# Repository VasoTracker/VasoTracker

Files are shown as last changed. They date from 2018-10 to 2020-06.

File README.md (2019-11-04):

VasoTracker
======
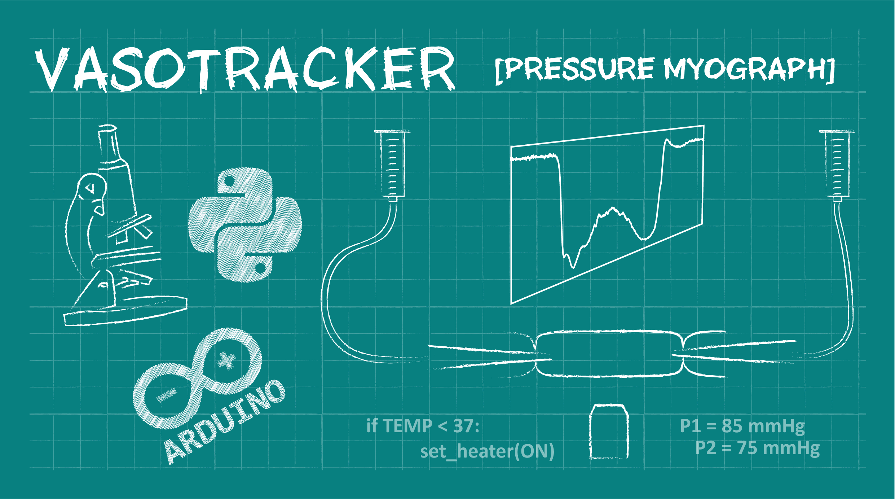
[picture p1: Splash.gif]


An open source pressure myograph system and diameter tracking software for assessing vascular reactivity.

Pressure myographs are used to assess blood vessel function. Both smooth muscle cell contraction and relaxation can be assayed using the pressure myograph.

Commercial pressure myograph systems are expensive. Rather than buy one, we prefered to build our own, taking advantage of open-source technologies and cheap off-the-shelf components. 

If you want to build your own myograph system, or simply want to try our software with an existing system, give VasoTracker a try. Its cheap (well its free) and it works.

## Paper
A paper describing the system in full, and demonstrating its use for studying vascular activity will hopefully be published in the very near future. We will place a link to the paper here: DOI:[10.3389/fphys.2019.00099](https://www.frontiersin.org/articles/10.3389/fphys.2019.00099/full)

# Contributors:
**University of Strathclyde:**
* Calum Wilson
* Matthew D Lee
* John G McCarron

**University of Durham:**
* Penelope F Lawton
* Christopher D Saunter
* John G Girkin

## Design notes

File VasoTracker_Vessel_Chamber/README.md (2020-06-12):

VasoTracker Vessel Chamber
======
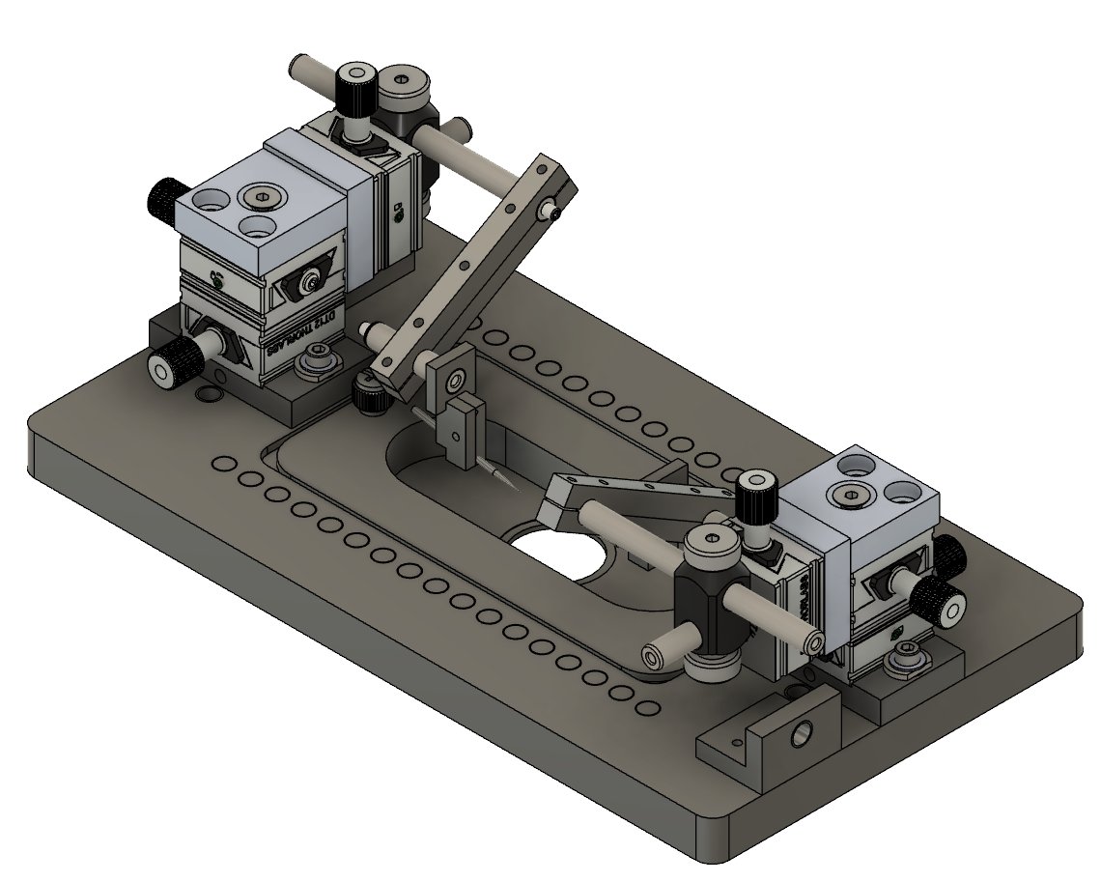
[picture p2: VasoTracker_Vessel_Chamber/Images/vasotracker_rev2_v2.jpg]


THIS IS VERSION 2 OF THE  VASOTRACKER CHAMBER. WE MAY HAVE MORE UPDATES - CHECKOUT THE VASOTRACKER WEBSITE:
http://www.vasotracker.com/downloads/pressure-myograph-hardware/

A cheap but effective vessel chamber for pressure myography. This repository contains the source files required to manufacture the Vessel Chamber.

We provide Creo (.prt), Fusion 360 (.f3d), STEP, and STL files. However, our parts were designed using Creo Parametric 4.0.  You'd be best to get a copy of Creo if you want to make any changes to the .prt files. PTC offer a free student edition: https://www.ptc.com/en/academic-program/products/free-software. However, if you only are happy with the chamber as it is then the .step files are all you need.

## Features

* **Designed for use on upright and inverted microscopes**

* **Precise alignment of cannula via 3-axis manipulators**

* **Magnetic mounts for perfusion plumbing and oxygenation**

## VasoTracker Chamber Parts:

The VasoTracker chamber can be built for less than £1300. The main chamber parts were custom designed and can be machined/3D-printed by in-house workshops or via commercial manufacturing services (e.g. Protolabs). Obviously, if you have access to a mechanical workshop, the system will be much cheaper than the price quoted below.

Here is a table of the custom components required:

  **Custom Imaging Chamber Parts**| **Material** |**Supplier**|**Part #**|**Qty**|**£/unit**|**Total (£)**
  :-----:|:-----:|:-----:|:-----:|:-----:|:-----:|:-----:
  ||||||
  Chamber base | POM-C/Delrin | Workshop / Protolabs | - | 1 |178.62|178.62
  Chamber insert | POM-C/Delrin ** | Workshop / Protolabs | - | 1 |95.48|95.48
  Leur connector blocks | POM-C/Delrin | Workshop / Protolabs | - | 2 |136.52|273.04
  Cannula fixture A | PETG/PLA | 3D Print | - | 2 | - | -
  Cannula fixture B | PETG/PLA | 3D Print | - | 2 | - | -
  Cannula Lateral Bottom | PETG/PLA | 3D Print | - | 2 | - | -
  Cannula Lateral Top | PETG/PLA | 3D Print | - | 2 | - | -
  Magnetic plumbing holders | SS or Delrin ** | Workshop / Protolabs | - | 2 | - | -
   ||||||
   | | | | | |**Subtotal**|**547.14**

* Prices correct June 2020. Obviously, they are subject to change.

Here are the other required components:

| Parts                                          | Supplier                | Part #      | Qty | £/unit   | Total (£) |
|------------------------------------------------|-------------------------|-------------|-----|----------|-----------|
|                                                |                         |             |     |          |           |
| Imaging Chamber                                |                         |             |     |          |           |
| 25mm diameter cover glass (100   pieces)       | Scientific Lab Supplies | MIC3320     | 1   | 18.66    | 18.66     |
| M3 thumb screws (Come in a   pack of 10)       | RS                      | 664-4637    | 1   | 4.7      | 4.7       |
|                                                |                         |             |     |          |           |
| Perfusion attachments                          |                         |             |     |          |           |
| 5mm diameter, 3mm thick disc magnets (50 pk)   | Amazon                  | B00TACMMP0  | 1   | 7.20     | 7.20      |
| 1.5", 14 - 18 Guage Blunt, bent needles        | Needlez                 | Selection   | -   | -        | -         |
| Superglue                                      | Amazon                  | B003CT4XT0  | 1   | 4.20     | 4.20      |
|                                                |                         |             |     |          |           |
| Cannula holders                                |                         |             |     |          |           |
| 3-axis translation stage                       | Thorlabs                | DT12XYZ/M   | 2   | 245.91   | 491.82    |
| Screw thread adapter                           | Thorlabs                | AP4M3M      | 2   | 1.58     | 3.16      |
| 13 mm metal rod                                | Thorlabs                | MS05R/M     | 2   | 4.79     | 9.58      |
| 25 mm metal rod                                | Thorlabs                | MS1R/M      | 2   | 5.08     | 10.16     |
| 75 mm metal rod                                | Thorlabs                | MS3R/M      | 2   | 6.34     | 12.68     |
| 90 degree rod clamp                            | Thorlabs                | MSRA90      | 2   | 13.39    | 26.78     |
| 1.5 mm OD glass capillary glass (225 pieces)   | Warner Instruments      | 30-0058     | 1   |          |           |
| M2 Screw & nut kit                             | Amazon                  | B07TNT5NMY  | 1   | 5.99     | 5.99      |
|                                                |                         |             |     |          |           |
| Tubing & Connectors                            |                         |             |     |          |           |
| Female luer  (threaded 1/16" barb; pack of 25) | Cole-Palmer             | GY-45502-30 | 1   | 8.53     | 8.53      |
| Masterflex 1.22 ID tubing (100   ft roll)      | Cole-Palmer             | WZ-06460-31 | 1   | 96       | 96        |
| Female luer (1/16" barb;   pack of 25)         | Cole-Palmer             | GY-45502-00 | 1   | 6.36     | 6.36      |
| Male luer (1/16" barb;   pack of 25)           | Cole-Palmer             | GY-45505-00 | 1   | 6.46     | 6.46      |
| Luer stopcock (pack of 10)                     | Cole-Palmer             | WZ-30600-02 | 1   | 16.94    | 16.94     |
|                                                |                         |             |     |          |           |
|                                                |                         |             |     | Subtotal | 712       |

* Prices correct June 2020. Obviously, they are subject to change.

## Building the VasoTracker Chamber:

 To build the VasoTracker chamber, all that is required it to connect the components together:

 1.	Seal the bottom of the chamber insert by securing a 25mm coverslip to the through-hole using superglue or vacuum grease.
 2.	Place the chamber insert in the chamber base and secure using 2 of the M3 thumb screws.
 3.	Secure the tubing anchors to the chamber base using M3 screws.
 4.	Secure 5 mm diameter magnets into the holes on the chamber base using superglue. You may want to ensure that the polarity of all of the magnets is the same.
 5.	Secure 5 mm diameter magnets into the bottom of plumbing holders using superglue. You may want to ensure that the polarity is correct.
 5.	Secure the mounts for the 3-axis positioning stages to the base using the included M6 screws. Then mount the 3-axis positioning stages.
 6. Connect the cannula holder parts to the 3-axis manipulators as shown below.
 7.	Mount glass cannula (pulled with pipette puller) onto cannula holder.
 8. Screw a threaded female luer (1/16" barb) into each of the tubing holders.
 9. Connected cannula to luer connector via tubing.
 10. Connect luer stopcock to each of the leur connectors to enable 3-way control of input and output.
 11. Securse bent needle perfusion plumbing in magnetic holders and the chamber is ready to be filled with physiological saline solution!

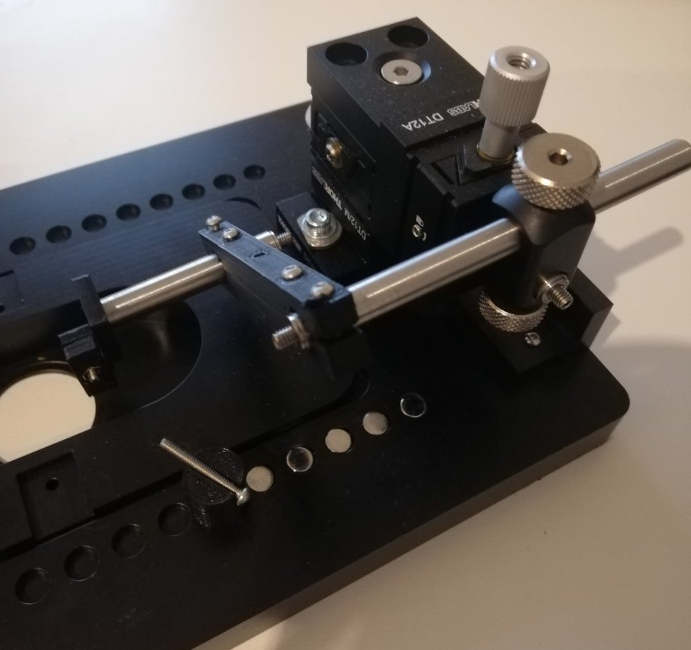
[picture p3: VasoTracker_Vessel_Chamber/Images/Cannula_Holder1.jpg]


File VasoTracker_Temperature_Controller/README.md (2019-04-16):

VasoTracker Temperature Controller
======


An Arduino-based temperature controller for the VasoTracker myograph system.

## Features

* **Reads and displays temperature sensed by an 10k NTC thermistor**

* **Implements bang-bang control of heating elements mounted on the VasoTracker Vessel Chamber**

* **Writes data to serial port for acquisition and display by the VasoTracker GUI**

## Required components:

The VasoTracker Temperature Controller (with temperature sensor and two heating elements) can be built for ~£75. Here is a table of the components required:

**Parts**|**Supplier**|**Part #**|**Qty**|**£/unit**|**Total (£)**
:-----:|:-----:|:-----:|:-----:|:-----:|:-----:
Arduino Uno|Arduino|A000066 |1|20.7|20.7
12V power supply|RS|903-7048|1|12.68|12.68
Arduino Proto Shield |Arduino|A000077|1|10|10
LCD Shield|iTead Studio|1602 LCD|1|3.98|3.98
10k NTC Thermistor|Adafruit|372|1|3.03|3.03
Kool-Pak 0.2Ω Thick Film (Heating) Resistor|Caddock|MP825.20.0-1%|2|6.89|13.78
NPN MOSFET|Infineon Technologies|IRL540NPBF|1|0.99|0.99
Resistor kit|Velleman-kit|RES-E12|1|4.7|4.7
Jumper wire kit|RobotShop|RB-Cix-02|1|3.77|3.77
2-pin Screw Terminal|RobotShop|RB-Dfr-465|3|0.6|1.8
Arduino R3 Stackable Headers|Sparkfun Electronics|PRT-10007|1|1.14|1.14
LEGO™ Encolsure|LEGO|-|-|-|-
 | | | |**Subtotal**|**76.57**

## Building the VasoTracker Temperature Controller:

To build the temperature controller, there is a little bit of soldering involved:

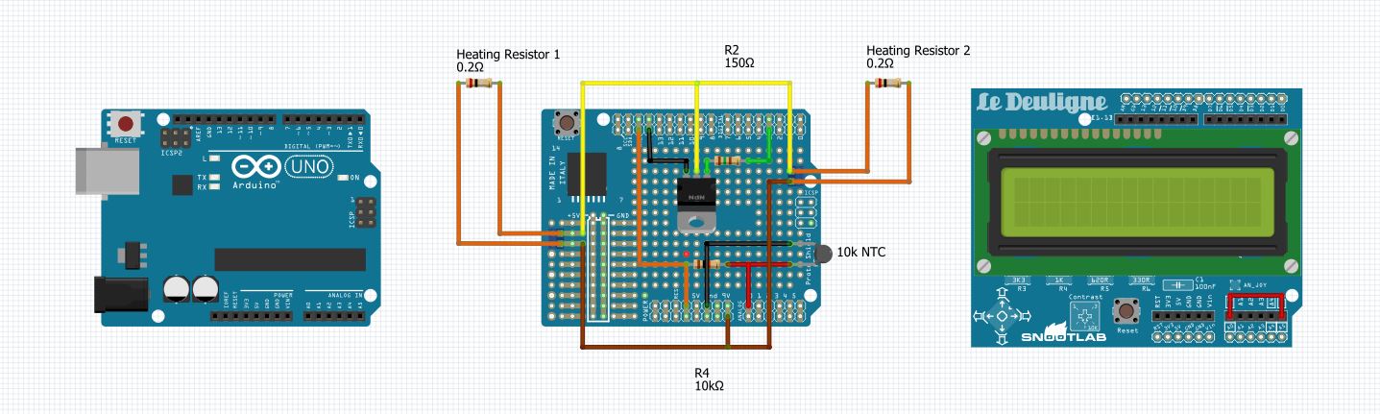
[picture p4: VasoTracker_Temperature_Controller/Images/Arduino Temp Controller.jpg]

</br>
Temperature controller schematic created using the breadboard view in Fritzing (http://fritzing.org/home/)

1.	Build the temperature sensor / heating circuit on the Arduino Proto shield, as shown in image above. Note that the heating elements (resistors) are connected to the Temperature controller via jumper cables and screw terminals mounted on the Proto Shield. Similarly, the temperature sensor is connected to a screw terminal mounted on the Proto Shield.
2.	Stack the completed Proto shield on top of the Arduino Uno.
3.	Place stackable headers on top of the Proto Shield (these are required to allow clearance for the pressure transducer connections and bend the A0 pin1 on the stackable header so that it does not connect to the Arduino Uno board.
4.	Stack the LCD Shield on top of the stackable headers.
5.	Use a female 1-pin jumper cable to connect the disconnected pin on the stackable header to the A5 pin on top of the LCD shield.
6.	 Wrap one end of a wire around the Arduino reset pin and another around Vin (5V).
7.	 Stack the LCD shield on top of the Arduino.
8.	 Connect a power supply to the ARDUINO device to switch the unit on. To supply sufficient power, it is recommended to use a 12V wall wort power supply, and to use the USB cable for data transmission.
9.	 Optionally, the device may be placed in an enclosure. We chose to build one from Lego® blocks because of their versatility .

**Notes:**
1. The A000077 Proto Shield is being discontinued. Many other suppliers sell equivalent prototyping boards (e.g. Adafruit 2077 Proto Shield).
2. For pictures of Step 3 onwards, check the similar instructions for the pressure controller here: https://github.com/VasoTracker/VasoTracker/tree/master/VasoTracker_Pressure_Monitor)**
2. The LCD shield uses the A0 pin for buttons. However, we (stupidly) connected our thermistor to A0. By bending the A0 pin on the stackable header and connecting it to A5 on the LCD shield, we are rerouting A0 on the LCD shield to A5 (thus enabling the thermistor to use A0). Obviously, by connecting the thermistor to A5, and altering the Arduino code, this step could be avoided!
3. Should prevent accidental resetting of the Arduino (which would be annoying if it occurred during an experiment)... connect reset pin to 5V via 120 ohm resistor
4. As an alternative to soldering the components onto the Arduino Proto Shield, an Arduino Proto Shield with Mini Breadboard could be used.

## Programming the VasoTracker Temperature Controller:

   * Download VasoTracker as a zip file and extract all files (if you don't have it already) from here: https://github.com/kaelome/VasoTracker
   * Download and install the Aruino IDE (Python 3.6) <https://www.arduino.cc/en/Guide/Windows#toc1>
   * Open the following Arduino file in the Arduino IDE: VasoTracker/VasoTracker_Temperature_Controller/VasoTracker_Temperature_Controller_Code/VasoTracker_Temperature_Controller_Code.ino
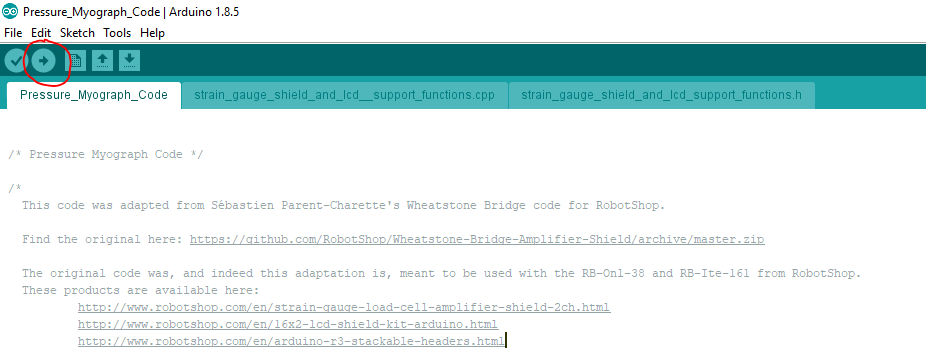
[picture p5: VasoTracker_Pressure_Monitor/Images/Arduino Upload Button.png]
   *	Upload code to the Arduino by clicking the upload button 

### Setting up the VasoTracker Temperature Controller:

  * Ensure heating elements are secured to the Vessel Chamber
  * Place temperature sensor in the Vessel Chamber (it is held in place by a magnetic clamp)
  * Connect the heating elements to the Temperature Controller.
  * Connect Temperature Controller to data acquisition computer via Arduino USB cable.
  * Connect 12V power supply to the Arduino
  * Adjust setpoint to desired temperature using LCD buttons

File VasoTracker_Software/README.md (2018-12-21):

VasoTracker diameter tracking software
======
Software for automatic diameter tracking in pressure myography experiments.

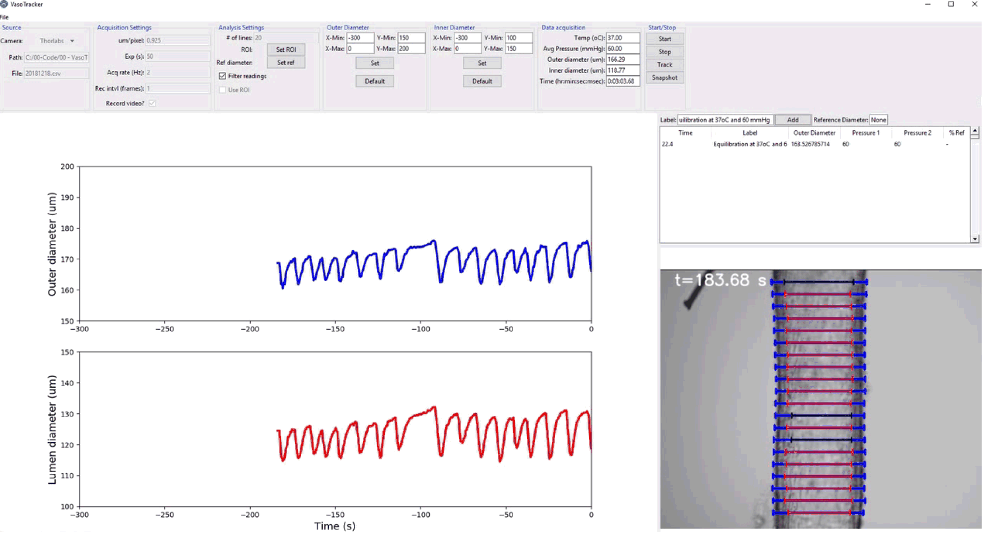
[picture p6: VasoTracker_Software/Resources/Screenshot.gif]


Written in [Python 2.7](https://www.python.org/ "Python 2.7"), and making use of [μManager](https://micro-manager.org/) camera control libraries

## Features

* **Acquires diameter measurements from pressurised blood vessels**

* **Live graphing of both outer and inner blood vessel diameter**

* **Diameter indicators overlaid on live image feed**

* **Synchronised data collection records and displays diameter, pressure, and temperature readings**

* **Record diameter measurements from up to 50 scan lines (you can examine propagated dilations)**

* **Line averaging: each scan line is integrated over 25 pixel lines to minimise errors introduced by contrast variances, the average diameter at each scanline is calculated and plotted**

* **Limit diameter tracking to a region of interest**

* **Filter of diameter measurements to exclude outlier data points**

* **Record and save image data throughout the experiment: VasoTracker outputs raw .tiff files, and .tiff files with diameter indicators overlaid**

* **All data is conveniently and automatically exported to .csv format**

* **Use with your own hardware! So long as your camera works with [μManager](https://micro-manager.org/), it can work with VasoTracker**

## Installing the VasoTracker Software:

A handy single-file installer and instructions for using the VasoTracker software is available to download at our [VasoTracker](http://www.vasotracker.com/downloads/) website.

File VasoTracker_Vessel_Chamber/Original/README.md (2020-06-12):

VasoTracker Vessel Chamber
======
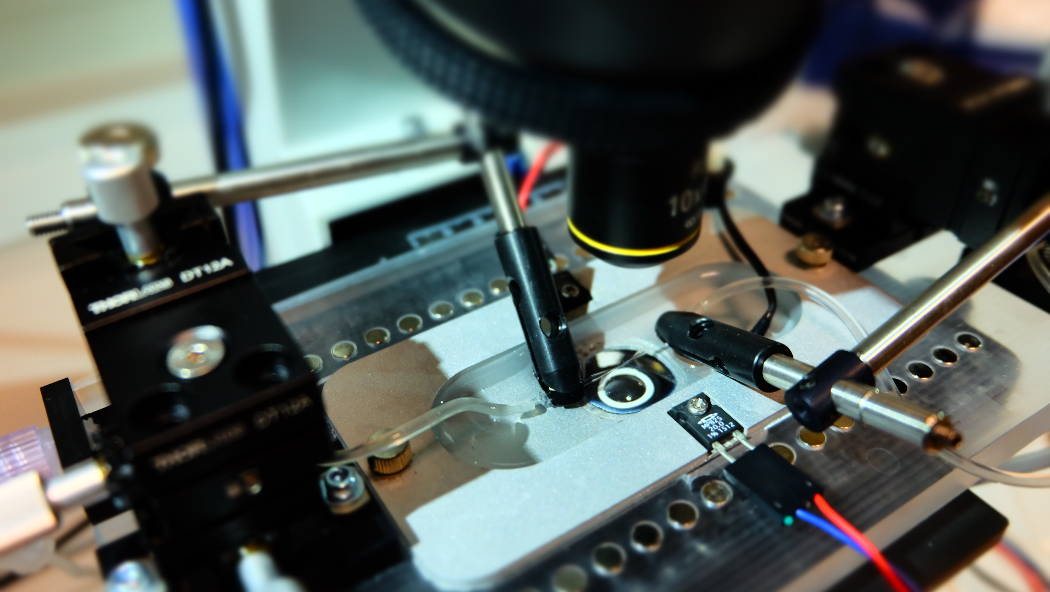
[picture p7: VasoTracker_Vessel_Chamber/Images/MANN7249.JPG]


## THIS IS THE ORIGINAL VASOTRACKER CHAMBER. FOR THE LATEST VASOTRACKER CHAMBER DESIGN, CHECKOUT THE VASOTRACKER WEBSITE:
http://www.vasotracker.com/downloads/pressure-myograph-hardware/

A cheap but effective vessel chamber for pressure myography. This repository contains the source files required to manufacture the Vessel Chamber.

These contents of this repository were designed using Creo Parametric 4.0. You'll need a copy of Creo if you want to make any changes to the .prt files. PTC offer a free student edition: https://www.ptc.com/en/academic-program/products/free-software. However, if you only are happy with the chamber as it is then the .step files are all you need.

## Features

* **Designed for use on upright and inverted microscopes**

* **Precise alignment of cannula via 3-axis manipulators**

* **Compatible with Built-in heating system:** (https://github.com/kaelome/VasoTracker/tree/master/VasoTracker_Temperature_Controller)

* **Magnetic mounts for perfusion plumbing and oxygenation**

## Building the VasoTracker Pressure Monitor:

The VasoTracker pressure monitor (with two inline pressure transducers) can be built for ~ £1500. The main chamber has been custom designed and can be machined by in-house workshops or via commercial manufacturing services (e.g. Protolabs). Obviously, if you have access to a mechanical workshop, the system will be much cheaper than the price quoted below.

Here is a table of the custom components required:

  **Custom Imaging Chamber Parts**| **Material** |**Supplier**|**Part #**|**Qty**|**£/unit**|**Total (£)**
  :-----:|:-----:|:-----:|:-----:|:-----:|:-----:|:-----:
  ||||||
  Chamber base | PMMA | Workshop / Protolabs | - | 1 |174.39|174.39
  Chamber insert | SS or Delrin ** | Workshop / Protolabs | - | 1 |144.21|144.21
  Tubing anchors | PMMA | Workshop / Protolabs | - | 2 |123.94|247.88
   ||||||
   | | | | |**Subtotal**|**442.54**

** This part should be machined from stainless steel (SS) if the VasoTracker Temperature Controller is to be used. If other temperature control methods will be used (e.g. externally heated perfusion solution), this part can be machined from Delrin (POM-C)

Here are the other required components:

| Parts                                          | Supplier                | Part #      | Qty | £/unit   | Total (£) |
|------------------------------------------------|-------------------------|-------------|-----|----------|-----------|
|                                                |                         |             |     |          |           |
| Imaging Chamber                                |                         |             |     |          |           |
| 25mm diameter cover glass (100   pieces)       | Scientific Lab Supplies | MIC3320     | 1   | 18.66    | 18.66     |
| M3 thumb screws (Come in a   pack of 10)       | RS                      | 664-4637    | 1   | 4.7      | 4.7       |
|                                                |                         |             |     |          |           |
| Perfusion attachments                          |                         |             |     |          |           |
| Neodynium disc magnets (In a   pack of 10)     | RS                      | 792-4559    | 4   | 4.15     | 16.6      |
| Magnetic Clamp for suction   tubes             | Warner Instruments      | MAG-2       | 4   | 45.00    | 180.00    |
|                                                |                         |             |     |          |           |
| Cannula holders                                |                         |             |     |          |           |
| 3-axis translation stage                       | Thorlabs                | DT12XYZ/M   | 2   | 231.80   | 463.60    |
| Screw thread adapter                           | Thorlabs                | AP4M3M      | 4   | 1.48     | 5.92      |
| 13 mm metal rod                                | Thorlabs                | MS05R/M     | 2   | 4.51     | 9.02      |
| 38 mm metal rod                                | Thorlabs                | MS1.5R/M    | 2   | 4.93     | 9.86      |
| 75 mm metal rod                                | Thorlabs                | MS3R/M      | 2   | 5.97     | 11.94     |
| 90 degree rod clamp                            | Thorlabs                | MSRA90      | 2   | 12.62    | 25.24     |
| 90 degree rod clamp                            | Thorlabs                | ER90B/M     | 2   | 10.71    | 21.42     |
| Cannula holder                                 | Siskiyou                | MSC-1 M     | 2   | 21.00    | 42.00     |
| 1.5 mm OD glass capillary   glass (225 pieces) | Harvard Apparatus       | 300058      |     |          |           |
|                                                |                         |             |     |          |           |
| Tubing & Connectors                            |                         |             |     |          |           |
| Female luer  (threaded 1/16" barb; pack of 25) | Cole-Palmer             | GY-45502-30 | 1   | 8.53     | 8.53      |
| Masterflex 1.22 ID tubing (100   ft roll)      | Cole-Palmer             | WZ-06460-31 | 1   | 96       | 96        |
| Female luer (1/16" barb;   pack of 25)         | Cole-Palmer             | GY-45502-00 | 1   | 6.36     | 6.36      |
| Male luer (1/16" barb;   pack of 25)           | Cole-Palmer             | GY-45505-00 | 1   | 6.46     | 6.46      |
| Luer stopcock (pack of 10)                     | Cole-Palmer             | WZ-30600-02 | 1   | 16.94    | 16.94     |
|                                                |                         |             |     |          |           |
|                                                |                         |             |     | Subtotal | 943.25    |

 To build the VasoTracker chamber, all that is required it to connect the components together:

 1.	Seal the bottom of the chamber insert by securing a 25mm coverslip to the through-hole using superglue or vacuum grease.
 2.	Place the chamber insert in the chamber base and secure using 2 of the M3 thumb screws.
 3.	Secure the tubing anchors to the chamber base using M3 screws.
 4.	Secure 10 mm diameter magnets into the holes on the chamber base using superglue. You may want to ensure that the polarity of all of the magnets is the same.
 5.	Secure the mounts for the 3-axis positioning stages to the base using the included M6 screws. Then mount the 3-axis positioning stages.
 6. Screw each of the cannula holders onto a 38 mm rod and couple to the 3-axis manipulators as shown below:
 7.	Mount glass cannula (pulled with pipette puller) onto cannula holder.
 8. Screw a threaded female luer (1/16" barb) into each of the tubing holders.
 9. Connected cannula to luer connector via tubing.
 10. Connect luer stopcock to each of the leur connectors to enable 3-way control of input and output.
 11. The chamber is now ready to be filled with physiological saline solution and have an artery mounted between the two cannula!

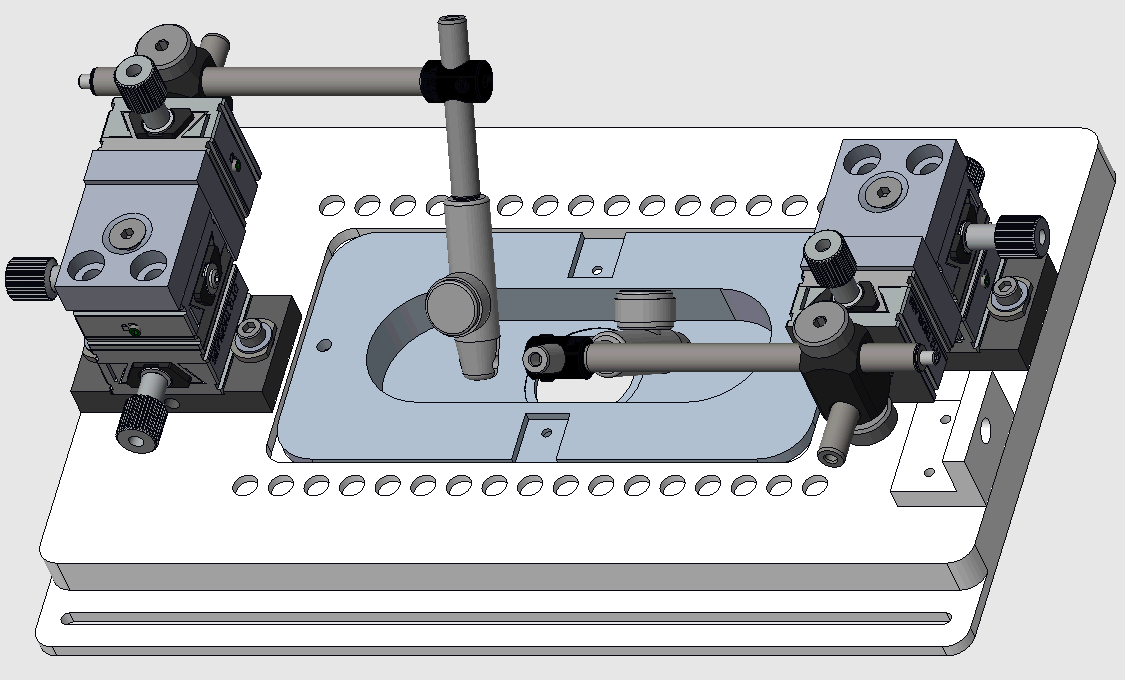
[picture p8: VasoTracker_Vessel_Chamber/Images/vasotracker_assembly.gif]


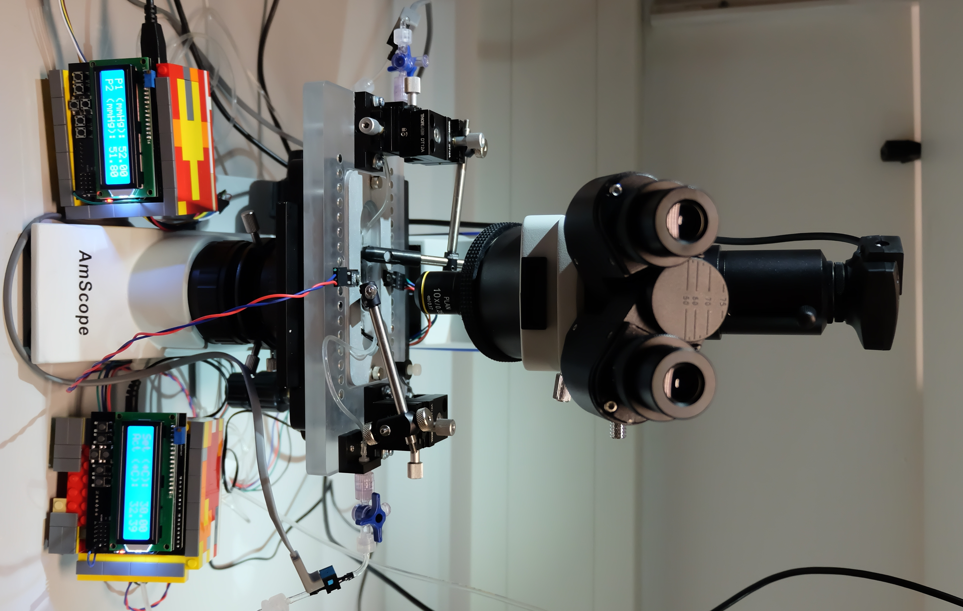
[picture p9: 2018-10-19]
VasoTracker_Vessel_Chamber/Images/MANN7244_cropped.jpg

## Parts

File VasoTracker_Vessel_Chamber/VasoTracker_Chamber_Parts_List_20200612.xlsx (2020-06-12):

Myograph Bath
Parts | Supplier | Part # / Description | Qty | £/unit | Total (£)
Custom Imaging Chamber Parts
Chamber | ProtoLabs | CNC Machine - POM-C, METRIC THREADING (SEE DRAWINGS FOR THREADING) | 1 | 178.62 | 178.62
Chamber insert | ProtoLabs | CNC Machine - POM-C, METRIC THREADING (SEE DRAWINGS FOR THREADING) | 1 | 95.48 | 95.48
Leur connector blocks | Protolabs | CNC Machine - POM-C, METRIC THREADING (SEE DRAWINGS FOR THREADING) | 2 | 136.52 | 273.04
Cannula fixture A | - | 3D Print (ETG/PLA) | 2 | - | - | 547.14
Cannula fixture B | - | 3D Print (ETG/PLA) | 2 | - | -
Cannula Lateral Bottom | - | 3D Print (ETG/PLA) | 2 | - | -
Cannula Lateral Top | - | 3D Print (ETG/PLA) | 2 | - | -
Magnetic plumbing holders | - | 3D Print (ETG/PLA) | 3 | - | -
Imaging Chamber Parts
25 mm Diameter No 1 Coverslips | Amazon | SLS MIC3320 | 1 | 18.66 | 18.66
M3 Thumb Screws, 6-10 mm long | Amazon | www.amazon.co.uk/sourcingmap%C2%AE-Computer-M3x7mm-Aluminum-Knurled/dp/B01NBDUK82/ | 1 | 5 | 5
Perfusion Attachments
50 Magnets | Amazon | 5mm diameter, 3 mm thick, www.amazon.co.uk/gp/product/B00TACMMP0 | 1 | 7.2 | 7.2
1.5", 14 - 18 Guage Blunt, bent needles | Needlez | For perfusion plumbing, get a selection, https://www.needlez.co.uk/product/16g-blunt-needle-1-5inch-38mm-bent-tip-90-deg | 2 | 0.63 | 1.26
Superglue | Amazon | Gorilla Glue, https://www.amazon.co.uk/Gorilla-4044205-Superglue-15g/dp/B003CT4XT0/ | 1 | 4.2 | 4.2
Cannula holders
3-axis MicroManipulator | Thorlabs | DT12XYZ/M | 2 | 245.91 | 491.82
Screw thread adapter | Thorlabs | AP4M3M | 2 | 1.58 | 3.16
13 mm metal rod | Thorlabs | MS05R/M | 2 | 4.79 | 9.58
25 mm metal rod | Thorlabs | MS1R/M | 2 | 5.08 | 10.16
75 mm metal rod | Thorlabs | MS3R/M | 2 | 6.34 | 12.68
90 degree clamp | Thorlabs | MSRA90 | 2 | 13.39 | 26.78
1.5 mm OD glass capillary glass (225 pieces) | Warner Instruments30-0058 |  | 1 | -
M2 Screw Kit | Amazon | Variety hex screws and nuts, www.amazon.co.uk/gp/product/B07TNT5NMY/ | 1 | 5.99 | 5.99
Tubing & Connectors
Female luer (threaded 1/16" barb; pack of 25) | Cole-Palmer | GY-45502-30 | 1 | 8.53 | 8.53
Masterflex 1.22 ID tubing (100 ft roll) | Cole-Palmer | WZ-06460-31 | 1 | 96 | 96
Female luer (1/16" barb; pack of 25) | Cole-Palmer | GY-45502-00 | 1 | 6.36 | 6.36
Male luer (1/16" barb; pack of 25) | Cole-Palmer | GY-45505-00 | 1 | 6.46 | 6.46
Luer stopcock (pack of 10) | Cole-Palmer | WZ-30600-02 | 1 | 16.94 | 16.94
 |  |  |  | Subtotal | 1277.92

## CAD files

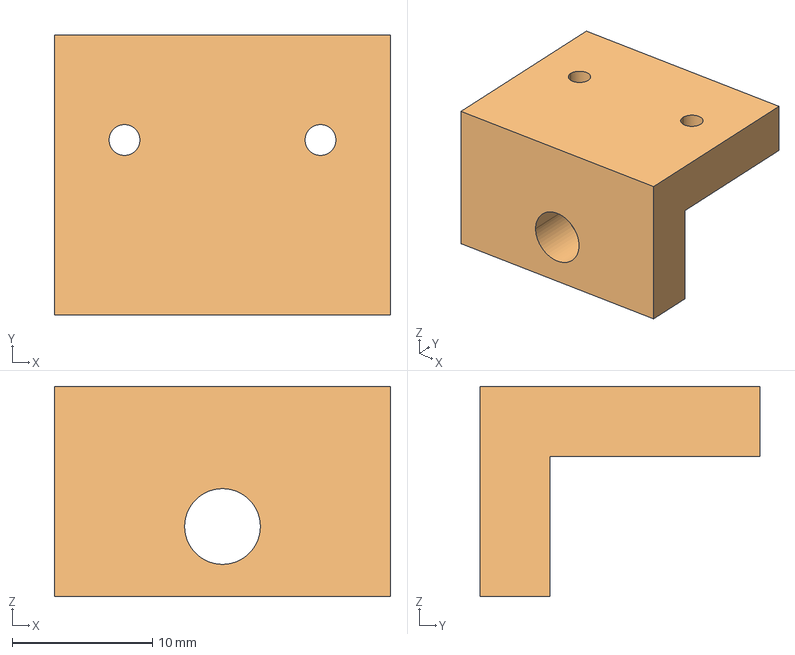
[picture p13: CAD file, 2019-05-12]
VasoTracker_Vessel_Chamber/Original/REV2/STEP/tubing_anchor.stp
24.0 x 20.0 x 15.0 mm

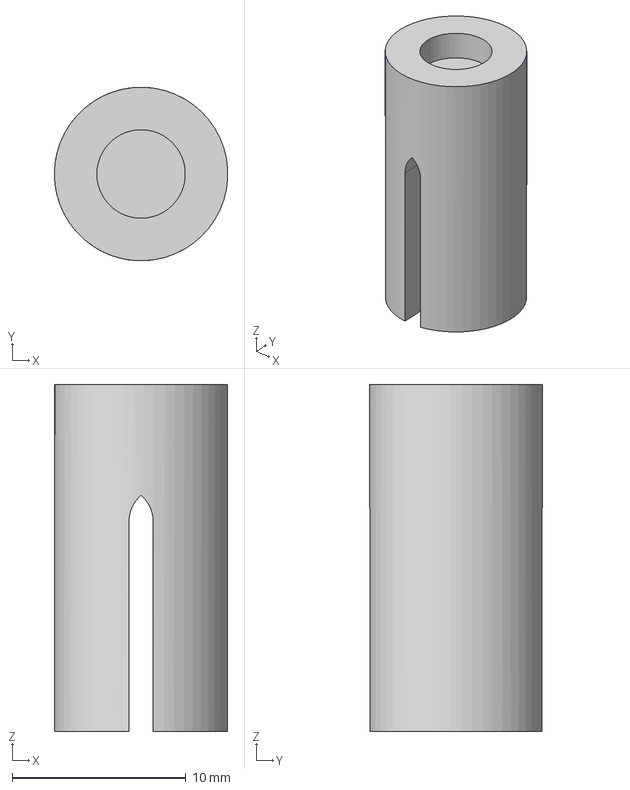
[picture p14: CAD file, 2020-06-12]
VasoTracker_Vessel_Chamber/Step/puming_holder_large v2.step
9.99 x 10.0 x 20.0 mm

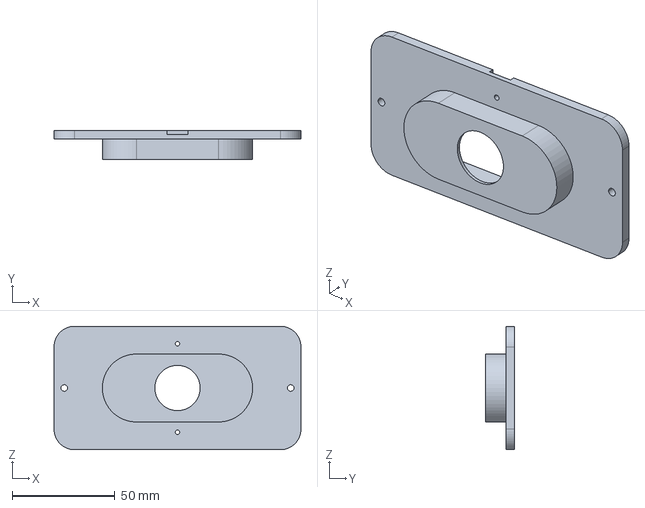
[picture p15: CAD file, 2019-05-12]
VasoTracker_Vessel_Chamber/Original/REV2/STEP/chamber_insert.stp
120.0 x 14.0 x 60.0 mm

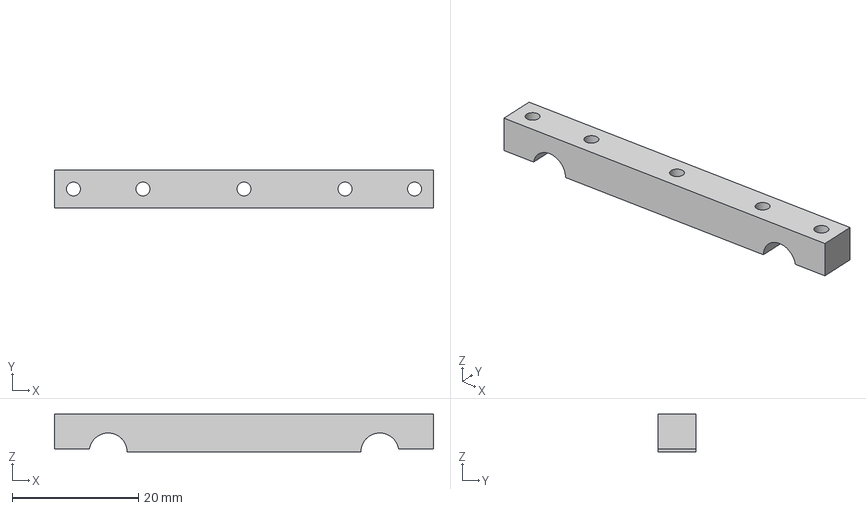
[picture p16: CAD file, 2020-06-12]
VasoTracker_Vessel_Chamber/Step/CANNULA_ARM_B v1.step
60.0 x 6.00 x 6.00 mm

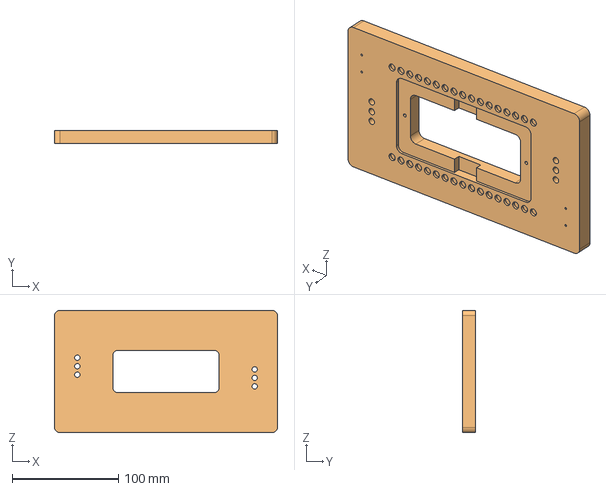
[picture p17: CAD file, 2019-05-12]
VasoTracker_Vessel_Chamber/Original/REV2/STEP/chamber_base.stp
210.0 x 12.0 x 115.0 mm

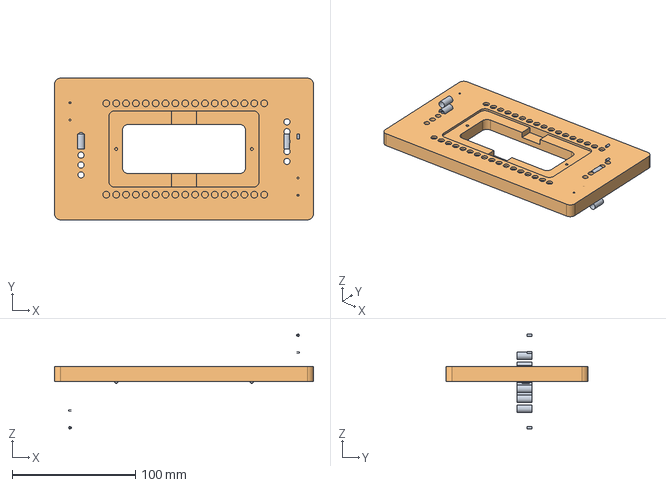
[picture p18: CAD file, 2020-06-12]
VasoTracker_Vessel_Chamber/Step/CHAMBER_BASE_REV2 v2.step
210.0 x 115.0 x 77.0 mm

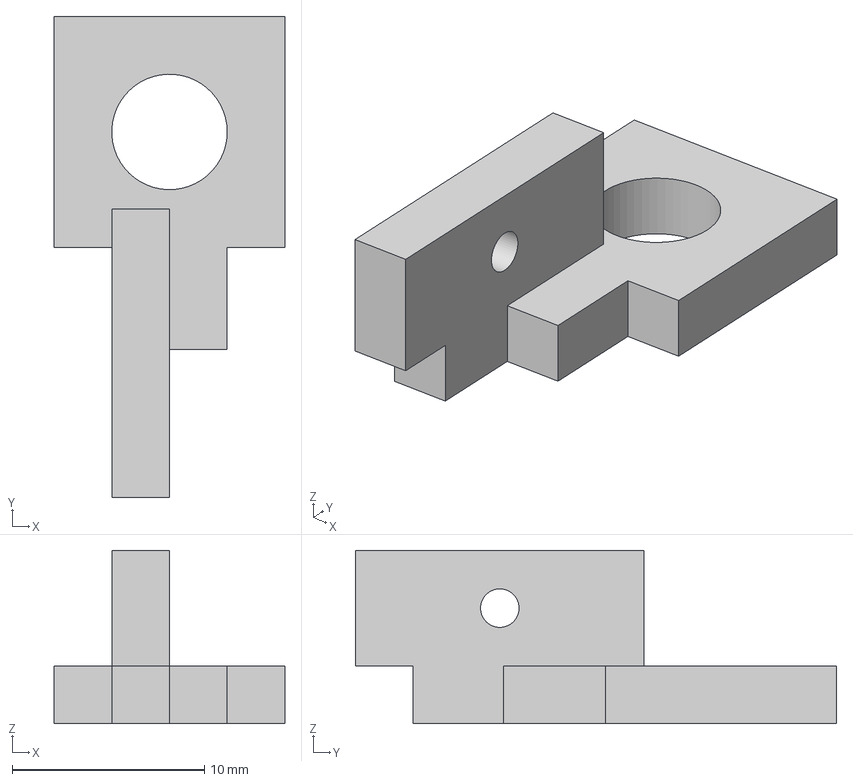
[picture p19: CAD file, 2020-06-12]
VasoTracker_Vessel_Chamber/Step/CANNULA_CLAMP_A v2.step
12.0 x 25.0 x 9.00 mm

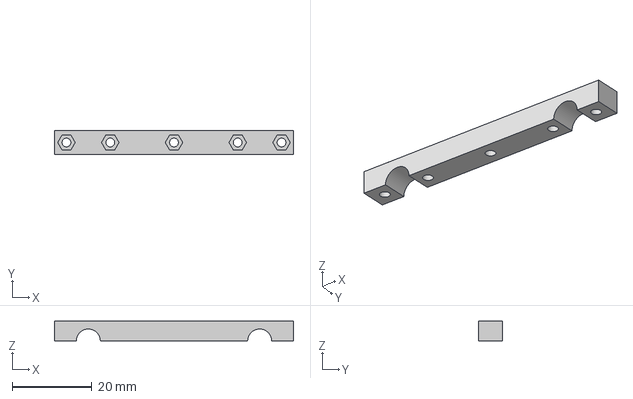
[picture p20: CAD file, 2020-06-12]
VasoTracker_Vessel_Chamber/Step/CANNULA_ARM_A v1.step
60.0 x 6.00 x 5.00 mm

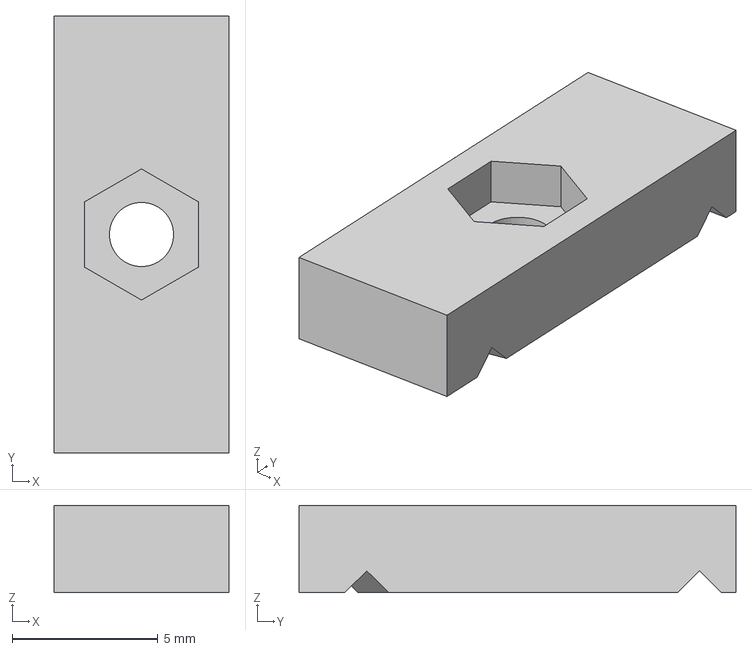
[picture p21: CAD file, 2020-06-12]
VasoTracker_Vessel_Chamber/Step/CANNULA_CLAMP_B v2.step
6.00 x 15.0 x 3.00 mm

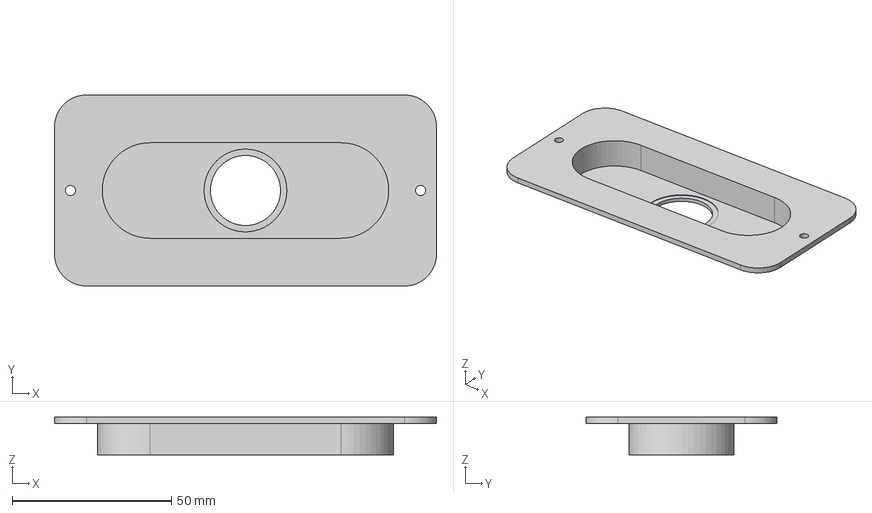
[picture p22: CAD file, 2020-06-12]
VasoTracker_Vessel_Chamber/Step/CHAMBER_INSERT_REV2_25ML v2.step
120.0 x 60.0 x 11.8 mm

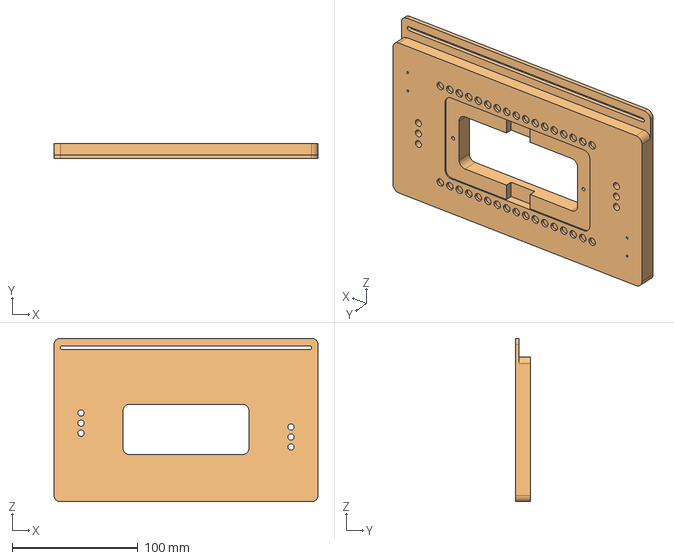
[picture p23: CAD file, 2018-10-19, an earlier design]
VasoTracker_Vessel_Chamber/Original/REV1/STEP/VasoTracker_ChamberBase.stp
210.0 x 12.0 x 130.0 mm

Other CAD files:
VasoTracker_Vessel_Chamber/Step/TUBING_ANCHOR v2.step
VasoTracker_Vessel_Chamber/Old_design/REV1/STEP/VasoTracker_TubingAnchor.stp
VasoTracker_Vessel_Chamber/Original/REV1/STEP/VasoTracker_TubingAnchor.stp
VasoTracker_Vessel_Chamber/Old_design/REV1/STEP/VasoTracker_ChamberInsert.stp
VasoTracker_Vessel_Chamber/Fusion 360/CANNULA_ARM_A v1.f3d
VasoTracker_Vessel_Chamber/Fusion 360/CANNULA_ARM_B v1.f3d
VasoTracker_Vessel_Chamber/Fusion 360/CANNULA_CLAMP_A v2.f3d
VasoTracker_Vessel_Chamber/Fusion 360/CANNULA_CLAMP_B v2.f3d
VasoTracker_Vessel_Chamber/Fusion 360/CHAMBER_BASE_REV2 v2.f3d
VasoTracker_Vessel_Chamber/Fusion 360/CHAMBER_INSERT_REV2_25ML v2.f3d
VasoTracker_Vessel_Chamber/Fusion 360/TUBING_ANCHOR v2.f3d
VasoTracker_Vessel_Chamber/Fusion 360/puming_holder_large v2.f3d
VasoTracker_Vessel_Chamber/Fusion 360/vasotracker_rev2 v2.f3d
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

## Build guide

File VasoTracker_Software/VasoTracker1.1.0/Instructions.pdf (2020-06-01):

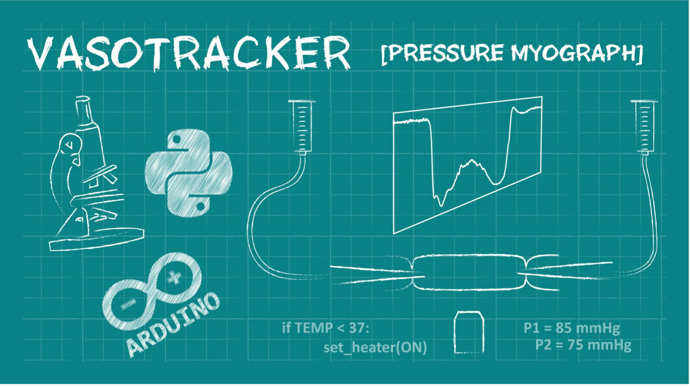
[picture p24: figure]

# Data Acquisition Software User Manual

15/11/2019

Developed at the University of Strathclyde and Durham University

www.vasotracker.com

# Table of Contents

I. Overview | 2

VasoTracker
Citing VasoTracker
The VasoTracker data acquisition software
The VasoTracker Offline Analyzer
II. | Installation | 4
| Hardware requirements
| Supported cameras Installation prerequisites
| Installing VasoTracker
III. | Running VasoTracker | 6
| Setting up a VasoTracker shortcut
| Maximizing VasoTracker performance Starting the VasoTracker Data Acquisition Software
IV. | VasoTracker Settings | 9
| The settings bar
| Source control panel Acquisition Settings control panel
| Analysis Settings control panel Outer and Inner Diameter Graph Settings control panel
| Data Acquisition panel Start/Stop panel
| Image dimension panel
V. VasoTracker Data Export | 13
| Data export Data entry table
VI. | Editing VasoTracker | 14
| Source code installation steps
| Installing Prerequisites
| Installing Python 2.7 Installing Python dependencies
| Launching VasoTracker from the source code

VASOTRACKER USER MANUAL V1 | 2

## Overview

VasoTracker

VasoTracker is an open source pressure myograph system for tracking the diameter of isolated, pressurized blood vessels. The complete system includes a vessel chamber, temperature controller, pressure monitor, microscope, camera, laptop computer, and analysis software – everything that is required to perform pressure myography.

We made VasoTracker because we wanted to make pressure myography more accessible (i.e. cheaper) and customizable. The full system costs ~$4500 (£3500 if you are in the UK). This is ~10% of the cost of a commercial myograph system. Visit the VasoTracker website (www.vasotracker.com) to find out how to build your own.

Citing VasoTracker

We hope that VasoTracker is of use to you or anyone else wishing to study blood vessel function. Our work developing and releasing VasoTracker as an open source platform was made possible by grant funding from the Wellcome Trust and British Heart Foundation. Our ability to support, develop and maintain VasoTracker will depend on more grants, so whether you use the VasoTracker software and hardware as a complete system or only the certain bit, please cite VasoTracker in your scientific publications.

Penelope F. Lawton, Matthew D. Lee, Christopher D. Saunter, John M. Girkin, John G. McCarron and Calum Wilson (2019). VasoTracker, a low-cost and open source pressure myograph system for vascular physiology. Frontiers in Physiology 10:99.
DOI: https://doi.org/10.3389/fphys.2019.00099

VASOTRACKER USER MANUAL V1 | 3

The VasoTracker data acquisition software

The VasoTracker data acquisition software was designed to monitor the diameter of blood vessels mounted in a pressure myograph. We developed the software to complement our own open source pressure myograph chamber, but it can be used to add diameter tracking capabilities to almost any microscope/camera set up. The software performs the following functions

- Live acquisition/display of pressurized arteries mounted in the VasoTracker vessel chamber.
- Real-time measurement and display of outer and inner artery diameter.
- Real-time measurement of bath temperature and intraluminal pressure.
- Live recording and graphing of artery diameter(s).
- Tracking of experimental manipulations (e.g. drug additions).
- Multi-line diameter tracking.
- Tracking within a user-specified region-of-interest (ROI).
- Line averaging and statistical filtering of result.
- Video output (.tiff files).

The VasoTracker Offline Analyzer

We also wrote some software for analyzing pre-recorded blood vessel data. Our offline analyzer can be used to assess vascular reactivity in blood vessels imaged using a variety of experimental techniques (pressure myography, fluorescence imaging, ultrasound). For more information and to download this software visit: http://www.vasotracker.com/blood-vessel-diameter-software/

The VasoTracker software is easy to adapt. Get in touch with us if you wish the software to calculate and output any other parameters (e.g. wall thickness, cross sectional area, media/lumen ratio). Alternatively, you can adapt the software yourself!

VASOTRACKER USER MANUAL V1 | 4

## Installation

Hardware requirements

VasoTracker is only compatible with 64-bit Windows operating systems. (well, we have only tested it on 64-bit operating systems)

- Microsoft Windows 10 Pro 64-bit
- 8GB RAM minimum (preferably 16GB)
- Compatible USB camera (see below)

Supported cameras

VasoTracker utilizes camera libraries provided by Micro-Manager (µManager) Open Source Microscopy Software (https://micro-manager.org/). If your camera works in µManager, then it should work with VasoTracker. We have fully tested, and use on our VasoTracker systems, the following cameras:

- Thorlabs DCC1545M USB 2.0 Camera
- OpenCV cameras
- FakeCamera – use to load your own images into VasoTracker

Installation prerequisites

Before installing VasoTracker, the camera drivers, Arduino IDE, and µManager must be installed. For the Thorlabs DCC1545M camera:
- Download and run the camera driver software from the Thorlabs website: https://www.thorlabs.com/software_pages/ViewSoftwarePage.cfm?Code=ThorCam
- Download and install the latest Nightly Build of µManager from the µManager website: http://valelab4.ucsf.edu/~MM/nightlyBuilds/1.4/Windows/
- Download and install the Arduino IDE from the Aduino website: https://www.arduino.cc/download_handler.php?f=/arduino-1.8.8-windows.exe

Ensure that µManager is installed to its default location: (C:\Program Files\Micro-Manager-1.4)

VASOTRACKER USER MANUAL V1 | 5

Installing VasoTracker

There are a number of options for installing VasoTracker:

Option 1 (easy installation method 1):
- Download and run the zipped MSI installer from the VasoTracker website: http://www.vasotracker.com/software/

Option 2 (easy installation method 2):
- Download the complete VasoTracker package from the GitHub repository: https://github.com/VasoTracker/VasoTracker
- Unzip the VasoTracker.zip package and navigate to the VasoTracker Software\VasoTracker1.x.x folder. Move or copy the folder to C:\Program Files.

We tried to make installing VasoTracker as simple as possible. But for reasons unknown to us, our installers fail on certain computer systems. If you are unlucky enough to own one of these, all is not lost. See Option 3 below!

Option 3 (not so easy installation method):
- Install the source code
- For instructions, refer to Editing VasoTracker (Page 14)

Choosing Option 3 will allow you to edit the VasoTracker code

VASOTRACKER USER MANUAL V1 | 6

## Running VasoTracker

VasoTracker may have been updated since this section was written. If it has, we should be updating these instructions soon. If you have any queries, send an email to vasotracker@gmail.com.

Setting up a VasoTracker shortcut

To set up a desktop shortcut:

- Navigate to the VasoTracker installation folder on your computer (the default location should be C:\Program Files\VasoTracker).
- Right click on the VasoTracker.exe
- Click “Send to”
- Click “Desktop”
- This action creates a desktop shortcut to the file or folder on your desktop.
- Make VasoTracker run in administrator mode (this ensures VasoTracker can save data files wherever you specify):
- Right-click the desktop shortcut, click “Advanced”, then check “Run as administrator”

Maximizing VasoTracker performance

We run VasoTracker on a number of different computer systems, on our less-able computers the following actions help performance:

- Using the “High Performance” Windows 10 power plan: https://help.ableton.com/hc/en-us/articles/115000211304-How-to-disable-power-throttling-on-Windows
- Disabling Windows USB Selective Suspend: https://www.windowscentral.com/how-prevent-windows-10-turning-usb-devices%3famp (https://www.windowscentral.com/how-prevent-windows-10-turning-usb-devices%3famp)
- Preventing Windows shutting off power to USB root hub: https://www.pcworld.com/article/3045567/how-to-keep-charging-your-usb-devices-past-your-pcs-bedtime.html (https://www.pcworld.com/article/3045567/how-to-keep-charging-your-usb-devices-past-your-pcs-bedtime.html)

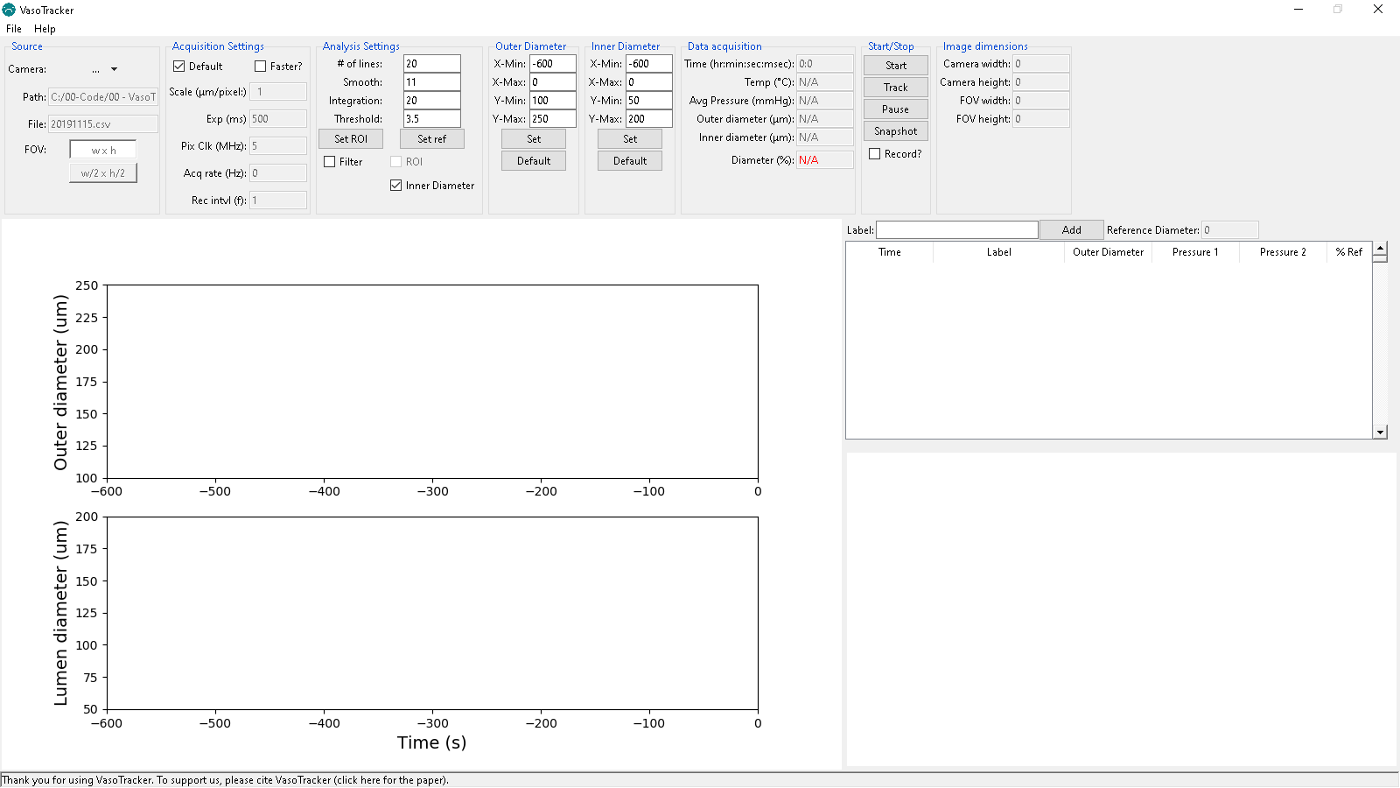
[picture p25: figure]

VASOTRACKER USER MANUAL V1 | 7

Starting the VasoTracker Data Acquisition Software

VasoTracker can be launched by any of the following methods:

- Double-clicking the desktop shortcut (created above).
- Double-clicking VasoTracker.exe in the installation folder
- Running VasoTracker.py from the python command line.

Upon launching, the VasoTracker software will prompt the user to create a .csv file for saving data. A “Save As” dialogue box will appear. The file name field is automatically populated with the current date in the default “Results” folder. However, the user may change the folder location and the filename.

If a csv file with the same name already exists, a warning will pop up and the user will be asked to confirm whether the existing file is to be replace. Selecting “Yes” will erase all data in the original file!

Once a save file has been created, VasoTracker will then launch with the default settings and you will be presented with the layout shown below.

Figure 1 – VasoTracker start screen

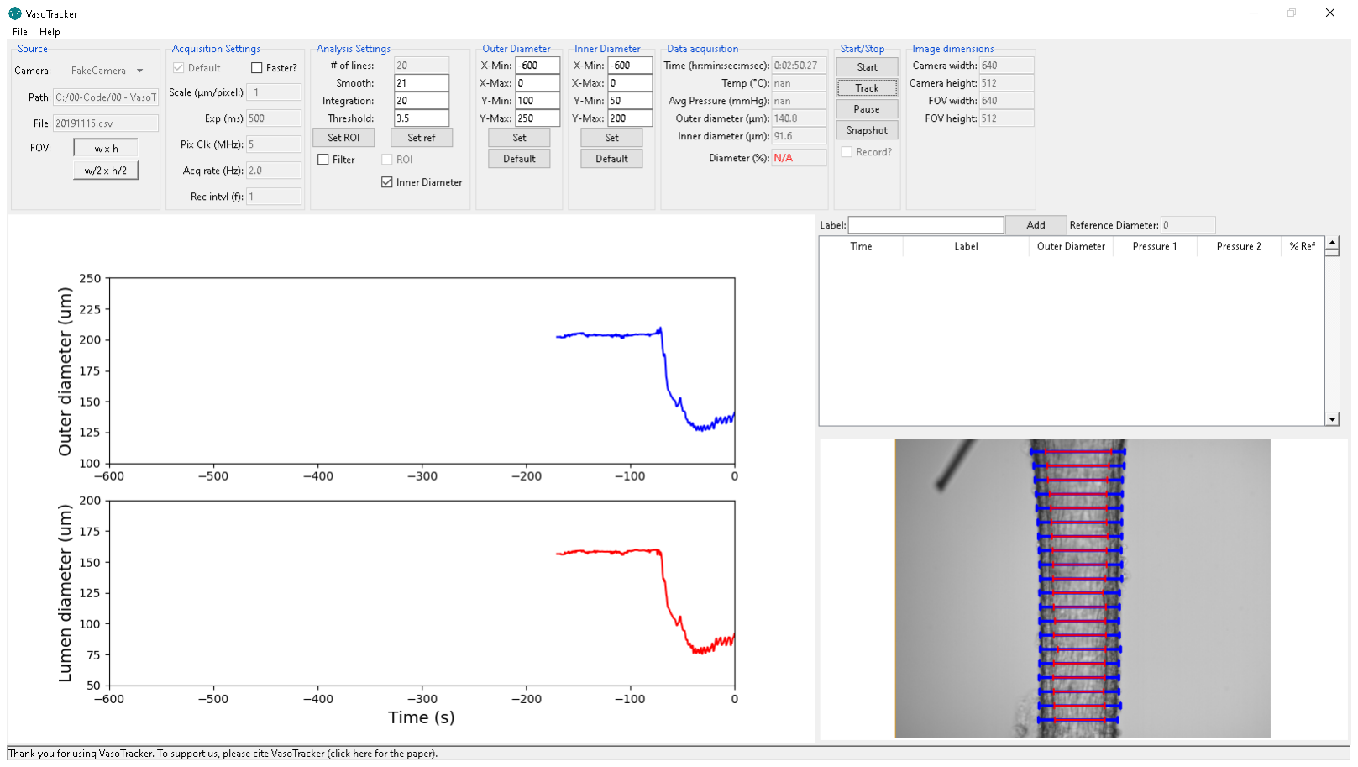
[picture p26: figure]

VASOTRACKER USER MANUAL V1 | 8

Demo Camera Mode

To familiarize users with the VasoTracker Data Acquisition Software, VasoTracker comes bundled with a fake/virtual camera adapter. This virtual camera adapter loads an example video recording of a pressurized artery and displays data as if a real camera is connected.

To run VasoTracker in Demo Mode:

- Enable the Virtual Camera by select “FakeCamera” in the “Source” panel.
- Start the virtual image acquisition by clicking “Start” in the “Start/Stop” panel.
- Begin diameter tracking by clicking “Record” in the “Start/Stop” panel.
- Once diameter tracking has initiated, diameter indicators will be overlaid on the camera feed box (Figure 2) and both inner and outer diameter will be plotted on the live graphs.

Figure 3 – Virtual Camera Mode with diameter tracking

Live Camera Mode

To run VasoTracker in live mode (i.e. acquiring images from a real camera)

- Load your camera by select “Thorlabs” in the “Source” panel.
- Start the image acquisition by clicking “Start” in the “Start/Stop” panel.
- Begin diameter tracking by clicking “Record” in the “Start/Stop” panel.

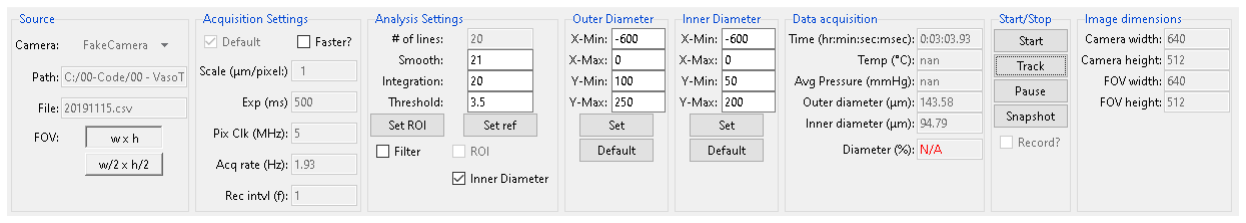
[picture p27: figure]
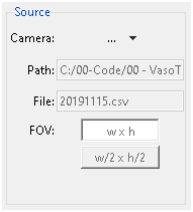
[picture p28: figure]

VASOTRACKER USER MANUAL V1 | 9

## VasoTracker Settings

VasoTracker may have been updated since this section was written. If it has, we should be updating these instructions soon. If you have any queries, send an email to vasotracker@gmail.com.

The settings bar

All of the acquisition and analysis settings can be altered in the settings bar. The settings bar also displays some handy information. Default settings can be changed by editing “default_settings.ini” in the root folder.

Figure 4 – VasoTracker settings bar

Source control panel

Figure 5 – Source settings

Camera: Select your camera here. If you are using a non-standard camera (you must have a working µManager config file), select µManagerCam. To use µManagerCam you mist place your µManager config file in the VasoTracker installation folder.

Path: displays the path to the current working directory.

File: displays the output file name.

FOV: buttons to set the field-of-view. This will only work for some cameras.

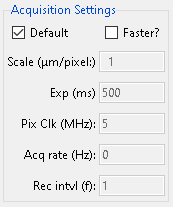
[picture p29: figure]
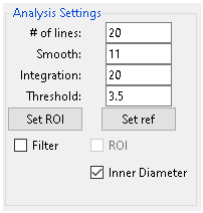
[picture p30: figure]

VASOTRACKER USER MANUAL V1 | 10

Acquisition Settings control panel

Figure 6 – Acquisition settings

Default: Enable/disable the default acquisition settings

Faster?: Enable/disable faster data acquisition here. This is still experimental.

Scale: Set the image calibration here. The default value of one will output diameter value in pixel units.

Exp: Set the camera exposure here.

Pix Clk: set the camera pixel clock here. We have only tested this with the Thorlabs camera. It allows more control over the exposure and frame rate.

Acq rate: displays the current acquisition rate.

Rec intvl: Set the interval (in frames) for exporting images here.

Analysis Settings control panel

Figure 7 – Analysis settings

# of lines: Set the number of scan lines here.

Smooth: Set how much smoothing is applied to intensity profiles (will improve wall detection).

Integration: Set the number of pixel lines over which diameter is integrated.

Threshold: Set threshold value for identifying outlier values

Set ROI: Click here to allow an ROI to be drawn on the display feed, diameter measurement will be limited to this ROI.

Set ref: Click here to set the current diameter as a reference value

Filter: Enable/disable outlier filtering

ROI: Enable/disable the ROI function.

Inner diameter: enable/disable inner diameter detection

When editing settings, you must confirm the values entered by hitting the “Enter” button on your keyboard.

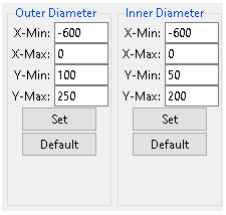
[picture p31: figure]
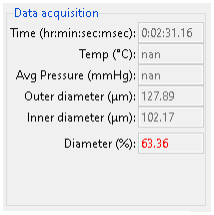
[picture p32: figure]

VASOTRACKER USER MANUAL V1 | 11

Outer and Inner Diameter Graph Settings control panel

Figure 8 – Graph settings

X-Min: Set the minimum x-axis (time) limit.

X-Max: Set the maximum x-axis (time) limit.

Y-Min: Set the minimum y-axis (diameter) limit.

Y-Max: Set the maximum y-axis (diameter) limit.

Set: Click here to allow an ROI to be drawn on the display feed, diameter measurement will be limited to this ROI.

Default: Click here to set the corresponding graph limits to default values.

All changes to graph settings must be confirmed by hitting the “Enter” button on your keyboard.

Data Acquisition panel

Figure 9 – Data display

Time: Displays the elapsed time (zeroed at beginning of experiment.

Temp: Displays the current temperature (from VasoTracker temperature controller).

Avg Pressure: Displays the vessel pressure (average of readings from VasoTracker pressure sensor).

Outer diameter: Displays the current inner diameter.

Inner diameter: Displays the current inner diameter.

Diameter: Displays the current (outer) diameter as a percentage of the reference diameter..

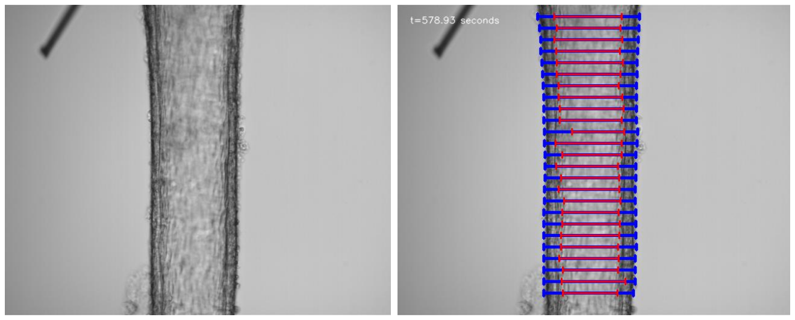
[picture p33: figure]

VASOTRACKER USER MANUAL V1 | 12

Start/Stop panel

Figure 10 – Start/stop panel

Start: Starts image acquisition.

Track: Starts the diameter tracking function.

Pause: Pauses diameter tracking (this enables settings to be altered).

Snapshot: Saves a snapshot of the current image display (with and without diameter indicators).

Record?: Enables/disables saving the image feed.

Figure 11 – Example saved images without (middle) and with (right)diameter indicators overlaid.

Image dimension panel

Figure 12 – Image dimensions

Camera width: Displays the width (in pixels) of the camera chip.

Camera height: Displays the height (in pixels) of the camera chip.

FOV width: Displays the width (in pixels) of the current field-of-view.

FOV height: Displays the height (in pixels) of the current field-of-view.

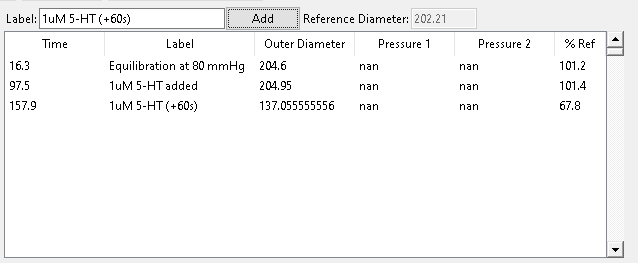
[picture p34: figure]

VASOTRACKER USER MANUAL V1 | 13

## VasoTracker Data Export

Data export

All data is saved automatically. On launching VasoTracker, the user is asked to create a .csv file. At each time point, all experimental parameters (time, diameter, pressure, temperature) are appended to the CSV file. Additionally, any data entered into the Data Entry Table (See below) is saved as an additional .csv file. The Data Entry Table .csv file is located in the folder specified.

Data entry table

To help in keeping track of experimental manipulations, VasoTracker includes a data entry table (Figure 13). The table allows the user to enter details of any experimental manipulations and provides a convenient measure of arterial tone at the time of each entry.

Figure 13 – Data entry table

VASOTRACKER USER MANUAL V1 | 14

## Editing VasoTracker

VasoTracker is written entirely in the Python programming language. Anybody can edit it in any way they see fit.

Source code installation steps

- Install the prerequisites
- Install Python 2.7 (Anaconda distribution)
- Install Python dependencies

Installing Prerequisites

Before installing VasoTracker, the camera drivers, Arduino IDE, and µManager must be installed. For the Thorlabs DCC1545M camera:

- Download and run the camera driver software from the Thorlabs website: https://www.thorlabs.com/software_pages/ViewSoftwarePage.cfm?Code=ThorCam
- Download and install the latest Nightly Build of µManager from the µManager website: http://valelab4.ucsf.edu/~MM/nightlyBuilds/1.4/Windows/
- Download and install the latest Nightly Build of µManager from the µManager website: http://valelab4.ucsf.edu/~MM/nightlyBuilds/1.4/Windows/

If you edit the VasoTracker source code you will need to run VasoTracker from the python command line or rebuild the application.

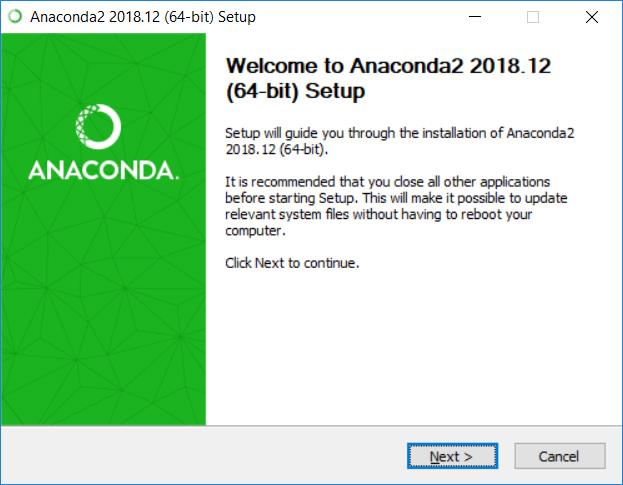
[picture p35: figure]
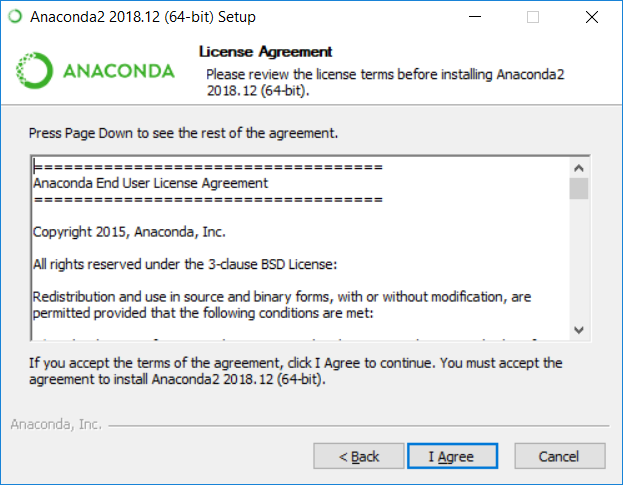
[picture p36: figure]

VASOTRACKER USER MANUAL V1 | 15

Installing Python 2.7

Should you wish to edit VasoTracker, you need to install Python 2.7. We recommend the Anaconda distribution. Once Python 2.7 has been installed, you also need a number of Python packages.

- Download the 64-bit Windows Anaconda distribution of Python 2.7 from the Anaconda website (we recommend Anaconda 2018.12): https://www.anaconda.com/distribution/
- Launch the installer and click “Next”
- Have a great time reading the License Agreement and click “I Agree”

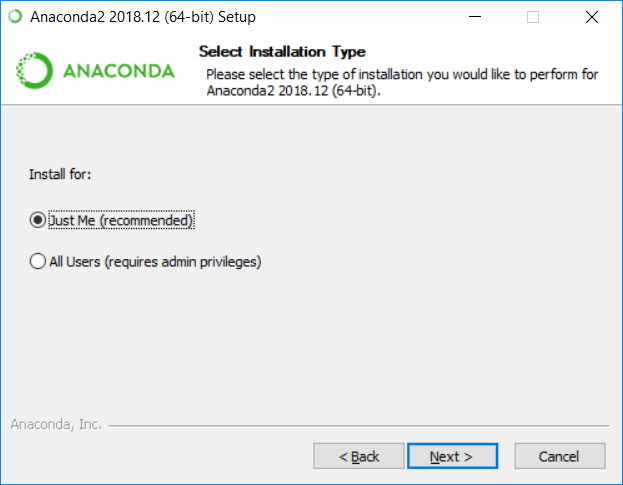
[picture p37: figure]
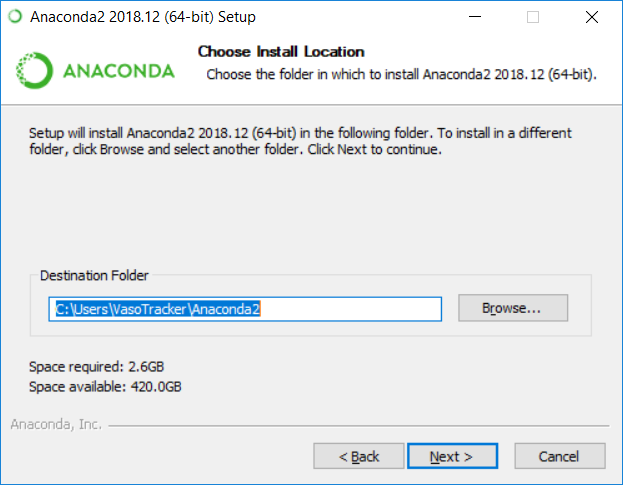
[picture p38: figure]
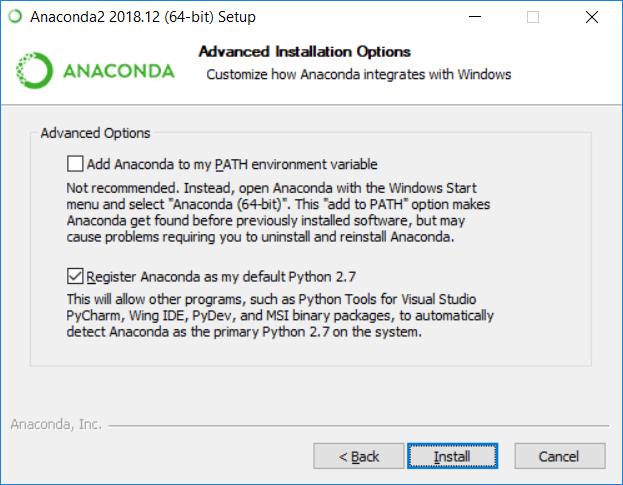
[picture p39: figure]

VASOTRACKER USER MANUAL V1 | 16
- Install for “Just Me”
- Choose the installation directory (and take a note of it)
- Register Anaconda as the default Python 2.7 (but do not add Anaconda to the PATH environment variable!)

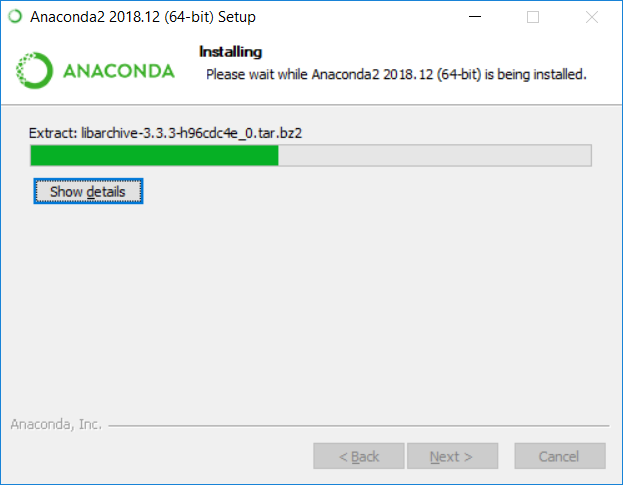
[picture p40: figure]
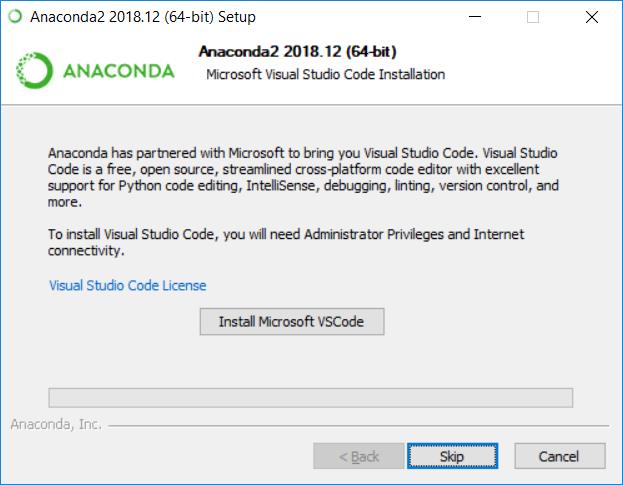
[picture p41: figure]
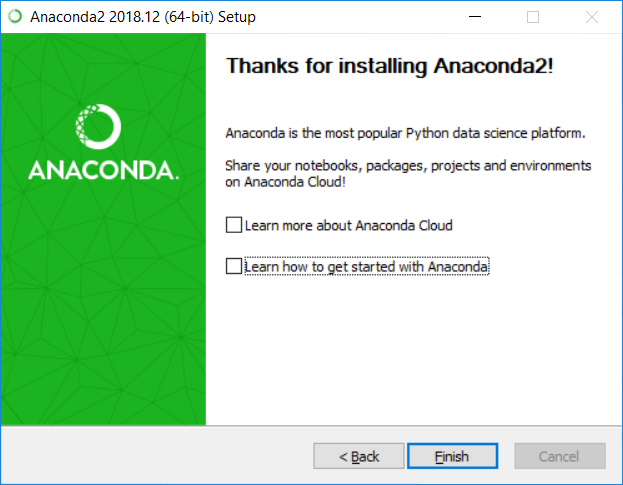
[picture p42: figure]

VASOTRACKER USER MANUAL V1 | 17
- Have two cups of tea whilst Anaconda installs
- If you want to edit the code, install Microsoft Visual Studio Code
- Click “Finish”

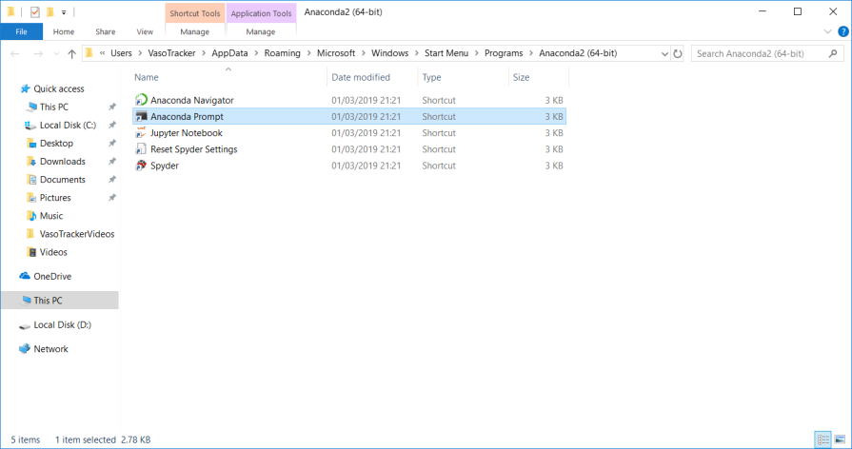
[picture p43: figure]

VASOTRACKER USER MANUAL V1 | 18
- Anaconda runs through a special command prompt. It is best to set this to run as administrator. First, locate the folder containing the Anaconda Prompt (search for “Anaconda Prompt” in windows search bar, right click, open file location)
- Right click on the anaconda prompt shortcut (you could also send this shortcut to the desktop, but perform the steps below by right clicking on the desktop shortcut)
- Click properties and open Shortcut tab, then click “Advanced” button
- Check “Run as administrator”

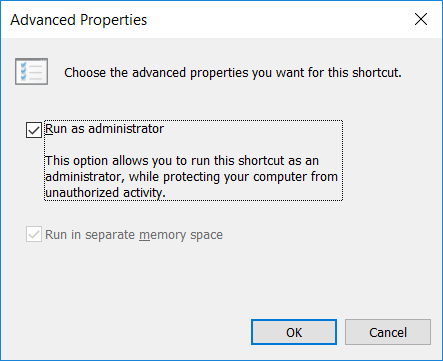
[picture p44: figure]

VASOTRACKER USER MANUAL V1 | 19

Installing Python dependencies

The recommended Anaconda distribution comes with most of the Python packages that are required by VasoTracker. Two packages must be installed separately, OpenCV and pyserial.

Installing OpenCV 3.4.1

- Download the OpenCV packaged (.exe file) from the official OpenCV site: https://sourceforge.net/projects/opencvlibrary/files/opencv-win/3.4.1/opencv-3.4.1-vc14_vc15.exe/download (https://sourceforge.net/projects/opencvlibrary/files/opencv-win/3.4.1/opencv-3.4.1-vc14_vc15.exe/download)
- Install OpenCV to C:/OpenCV/
- From the OpenCV directory, copy “cv2.pyd” from:

C:\opencv\build\python\2.7\x64

to the following Anaconda directory:

C:\Users\%Username%\Anaconda2\Lib\site-packages

The Anaconda directory may be in the C:Users\AppData hidden folder. We told you to take a note of it!

Installing pyserial

- Launch Anaconda Prompt

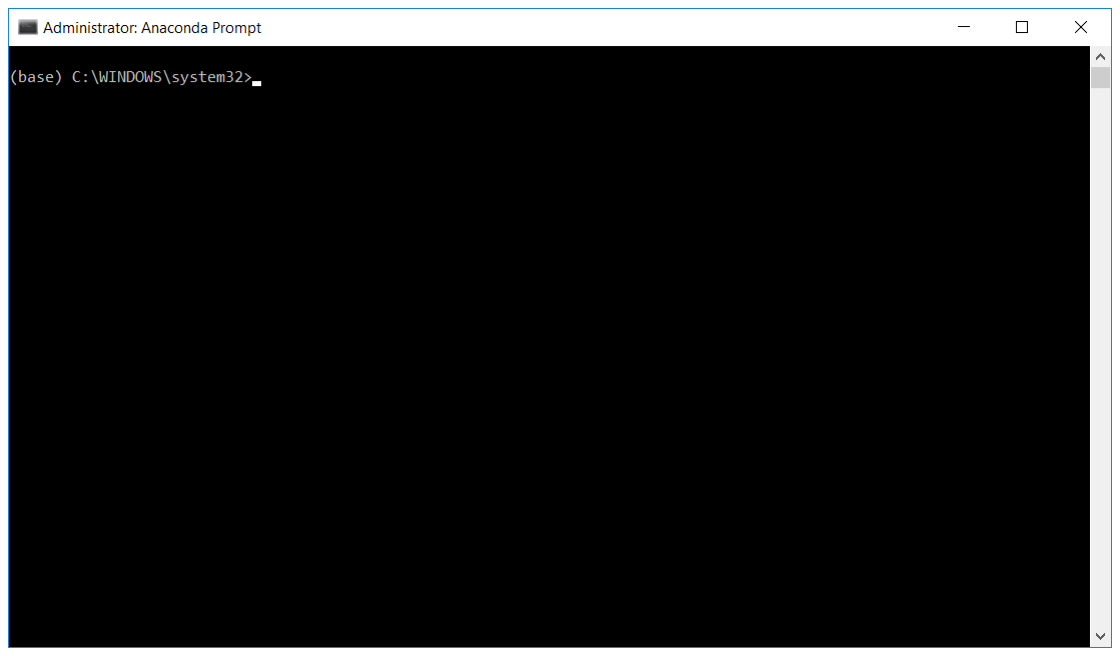
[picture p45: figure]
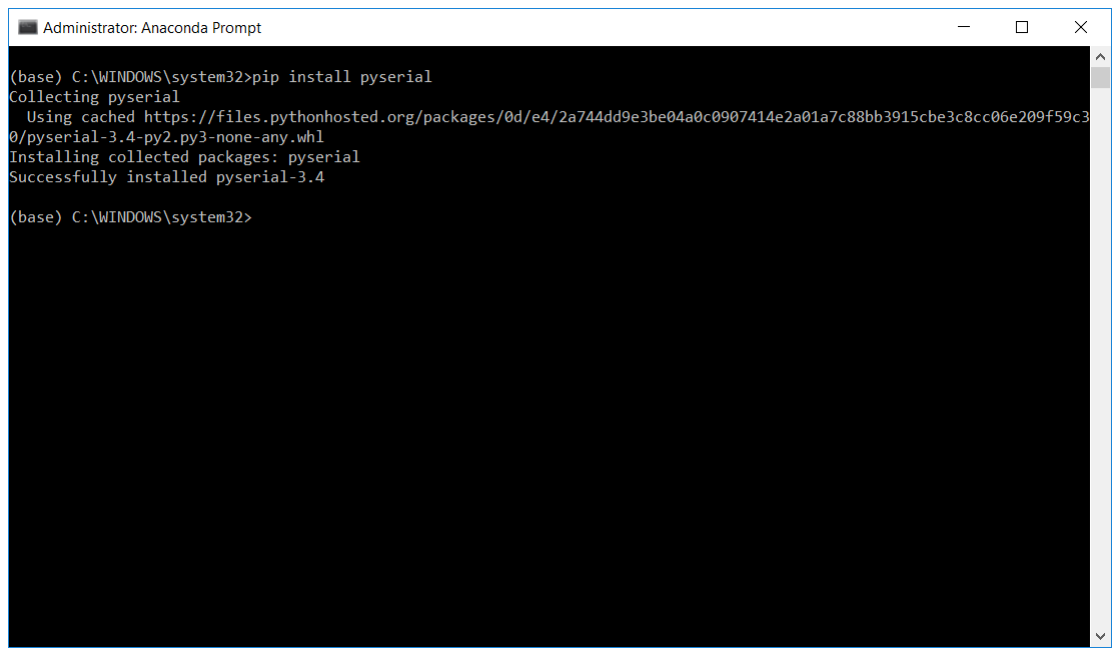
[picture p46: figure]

VASOTRACKER USER MANUAL V1 | 20
- Type the following command into the terminal and hit enter:

pip install pyserial

Congratulations if you made it this far, you should now be able to adapt the VasoTracker source code using Visual Studio Code, or any other editor.

Launching VasoTracker from the source code

VasoTracker should be launched from the Anaconda Prompt.

- Launch Anaconda Prompt

VASOTRACKER USER MANUAL V1 | 21
- Navigate to the VasoTracker source code folder using the “cd” command, by typing the following into the prompt and hitting enter:

cd c:\VasoTracker-master\VasoTracker_Software\Source

- Launch VasoTracker by typing the following into the prompt and hitting enter:

python vasotracker.py

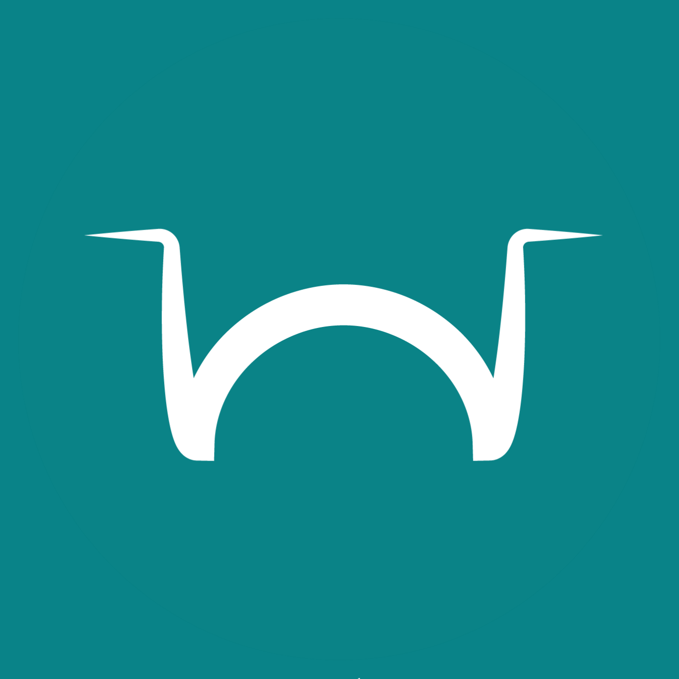
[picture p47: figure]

www.vasotracker.com

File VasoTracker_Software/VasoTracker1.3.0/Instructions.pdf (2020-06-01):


# Data Acquisition Software User Manual

28/05/2020

Developed at the University of Strathclyde and Durham University

www.vasotracker.com

# Table of Contents

I. Overview | 2

VasoTracker
Citing VasoTracker
The VasoTracker data acquisition software
The VasoTracker Offline Analyzer
II. | Installation | 4
| Hardware requirements
| Supported cameras Installation prerequisites
| Installing VasoTracker
III. | Running VasoTracker | 6
| Setting up a VasoTracker shortcut
| Maximizing VasoTracker performance Starting the VasoTracker Data Acquisition Software
IV. | VasoTracker Settings | 9
| The settings bar
| Source control panel Acquisition Settings control panel
| Analysis Settings control panel Outer and Inner Diameter Graph Settings control panel
| Data Acquisition panel Start/Stop panel
| Image dimension panel
V. VasoTracker Data Export | 14
| Data export Data entry table
VI. | Editing VasoTracker | 15
| Source code installation steps
| Installing Prerequisites
| Installing Python 2.7 Installing Python dependencies
| Launching VasoTracker from the source code

VASOTRACKER USER MANUAL V1 | 2

## Overview

VasoTracker

VasoTracker is an open source pressure myograph system for tracking the diameter of isolated, pressurized blood vessels. The complete system includes a vessel chamber, temperature controller, pressure monitor, microscope, camera, laptop computer, and analysis software – everything that is required to perform pressure myography.

We made VasoTracker because we wanted to make pressure myography more accessible (i.e. cheaper) and customizable. The full system costs ~$4500 (£3500 if you are in the UK). This is ~10% of the cost of a commercial myograph system. Visit the VasoTracker website (www.vasotracker.com) to find out how to build your own.

Citing VasoTracker

We hope that VasoTracker is of use to you or anyone else wishing to study blood vessel function. Our work developing and releasing VasoTracker as an open source platform was made possible by grant funding from the Wellcome Trust and British Heart Foundation. Our ability to support, develop and maintain VasoTracker will depend on more grants, so whether you use the VasoTracker software and hardware as a complete system or only the certain bit, please cite VasoTracker in your scientific publications.

Penelope F. Lawton, Matthew D. Lee, Christopher D. Saunter, John M. Girkin, John G. McCarron and Calum Wilson (2019). VasoTracker, a low-cost and open source pressure myograph system for vascular physiology. Frontiers in Physiology 10:99.
DOI: https://doi.org/10.3389/fphys.2019.00099

VASOTRACKER USER MANUAL V1 | 3

The VasoTracker data acquisition software

The VasoTracker data acquisition software was designed to monitor the diameter of blood vessels mounted in a pressure myograph. We developed the software to complement our own open source pressure myograph chamber, but it can be used to add diameter tracking capabilities to almost any microscope/camera set up. The software performs the following functions

- Live acquisition/display of pressurized arteries mounted in the VasoTracker vessel chamber.
- Real-time measurement and display of outer and inner artery diameter.
- Real-time measurement of bath temperature and intraluminal pressure.
- Live recording and graphing of artery diameter(s).
- Tracking of experimental manipulations (e.g. drug additions).
- Multi-line diameter tracking.
- Tracking within a user-specified region-of-interest (ROI).
- Line averaging and statistical filtering of result.
- Video output (.tiff files).

The VasoTracker Offline Analyzer

We also wrote some software for analyzing pre-recorded blood vessel data. Our offline analyzer can be used to assess vascular reactivity in blood vessels imaged using a variety of experimental techniques (pressure myography, fluorescence imaging, ultrasound). For more information and to download this software visit: http://www.vasotracker.com/blood-vessel-diameter-software/

The VasoTracker software is easy to adapt. Get in touch with us if you wish the software to calculate and output any other parameters (e.g. wall thickness, cross sectional area, media/lumen ratio). Alternatively, you can adapt the software yourself!

VASOTRACKER USER MANUAL V1 | 4

## Installation

Hardware requirements

VasoTracker is only compatible with 64-bit Windows operating systems. (well, we have only tested it on 64-bit operating systems)

- Microsoft Windows 10 Pro 64-bit
- 8GB RAM minimum (preferably 16GB)
- Compatible USB camera (see below)

Supported cameras

VasoTracker utilizes camera libraries provided by Micro-Manager (µManager) Open Source Microscopy Software (https://micro-manager.org/). If your camera works in µManager, then it should work with VasoTracker. We have fully tested, and use on our VasoTracker systems, the following cameras:

- Thorlabs DCC1545M USB 2.0 Camera
- OpenCV cameras
- FakeCamera – use to load your own images into VasoTracker

Installation prerequisites

Before installing VasoTracker, the camera drivers, Arduino IDE, and µManager must be installed. For the Thorlabs DCC1545M camera:
- Download and run the camera driver software from the Thorlabs website: https://www.thorlabs.com/software_pages/ViewSoftwarePage.cfm?Code=ThorCam
- Download and install the latest Nightly Build of µManager from the µManager website: http://valelab4.ucsf.edu/~MM/nightlyBuilds/1.4/Windows/
- Download and install the Arduino IDE from the Aduino website: https://www.arduino.cc/download_handler.php?f=/arduino-1.8.8-windows.exe

Ensure that µManager is installed to its default location: (C:\Program Files\Micro-Manager-1.4)

VASOTRACKER USER MANUAL V1 | 5

Installing VasoTracker

There are a number of options for installing VasoTracker:

Option 1 (easy installation method 1):
- Download and run the zipped MSI installer from the VasoTracker website: http://www.vasotracker.com/software/

Option 2 (easy installation method 2):
- Download the complete VasoTracker package from the GitHub repository: https://github.com/VasoTracker/VasoTracker
- Unzip the VasoTracker.zip package and navigate to the VasoTracker Software\VasoTracker1.x.x folder. Move or copy the folder to C:\Program Files.

We tried to make installing VasoTracker as simple as possible. But for reasons unknown to us, our installers fail on certain computer systems. If you are unlucky enough to own one of these, all is not lost. See Option 3 below!

Option 3 (not so easy installation method):
- Install the source code
- For instructions, refer to Editing VasoTracker (Page 15)

Choosing Option 3 will allow you to edit the VasoTracker code

VASOTRACKER USER MANUAL V1 | 6

## Running VasoTracker

VasoTracker may have been updated since this section was written. If it has, we should be updating these instructions soon. If you have any queries, send an email to vasotracker@gmail.com.

Setting up a VasoTracker shortcut

To set up a desktop shortcut:

- Navigate to the VasoTracker installation folder on your computer (the default location should be C:\Program Files\VasoTracker).
- Right click on the VasoTracker.exe
- Click “Send to”
- Click “Desktop”
- This action creates a desktop shortcut to the file or folder on your desktop.
- Make VasoTracker run in administrator mode (this ensures VasoTracker can save data files wherever you specify):
- Right-click the desktop shortcut, click “Advanced”, then check “Run as administrator”

Maximizing VasoTracker performance

We run VasoTracker on a number of different computer systems, on our less-able computers the following actions help performance:

- Using the “High Performance” Windows 10 power plan: https://help.ableton.com/hc/en-us/articles/115000211304-How-to-disable-power-throttling-on-Windows
- Disabling Windows USB Selective Suspend: https://www.windowscentral.com/how-prevent-windows-10-turning-usb-devices%3famp (https://www.windowscentral.com/how-prevent-windows-10-turning-usb-devices%3famp)
- Preventing Windows shutting off power to USB root hub: https://www.pcworld.com/article/3045567/how-to-keep-charging-your-usb-devices-past-your-pcs-bedtime.html (https://www.pcworld.com/article/3045567/how-to-keep-charging-your-usb-devices-past-your-pcs-bedtime.html)

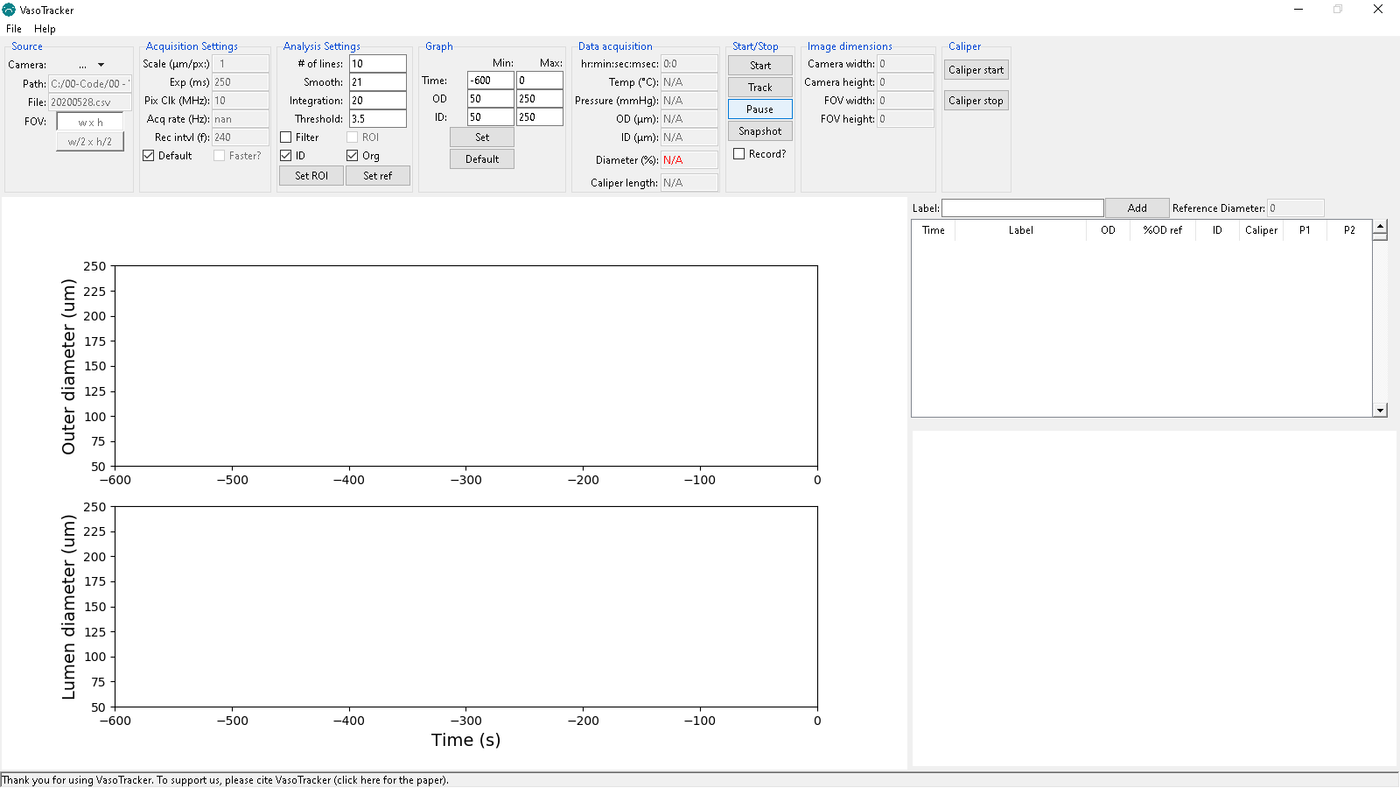
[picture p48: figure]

VASOTRACKER USER MANUAL V1 | 7

Starting the VasoTracker Data Acquisition Software

VasoTracker can be launched by any of the following methods:

- Double-clicking the desktop shortcut (created above).
- Double-clicking VasoTracker.exe in the installation folder
- Running VasoTracker.py from the python command line.

Upon launching, the VasoTracker software will prompt the user to create a .csv file for saving data. A “Save As” dialogue box will appear. The file name field is automatically populated with the current date in the default “Results” folder. However, the user may change the folder location and the filename.

If a csv file with the same name already exists, a warning will pop up and the user will be asked to confirm whether the existing file is to be replace. Selecting “Yes” will erase all data in the original file!

Once a save file has been created, VasoTracker will then launch with the default settings and you will be presented with the layout shown below.

Figure 1 – VasoTracker start screen

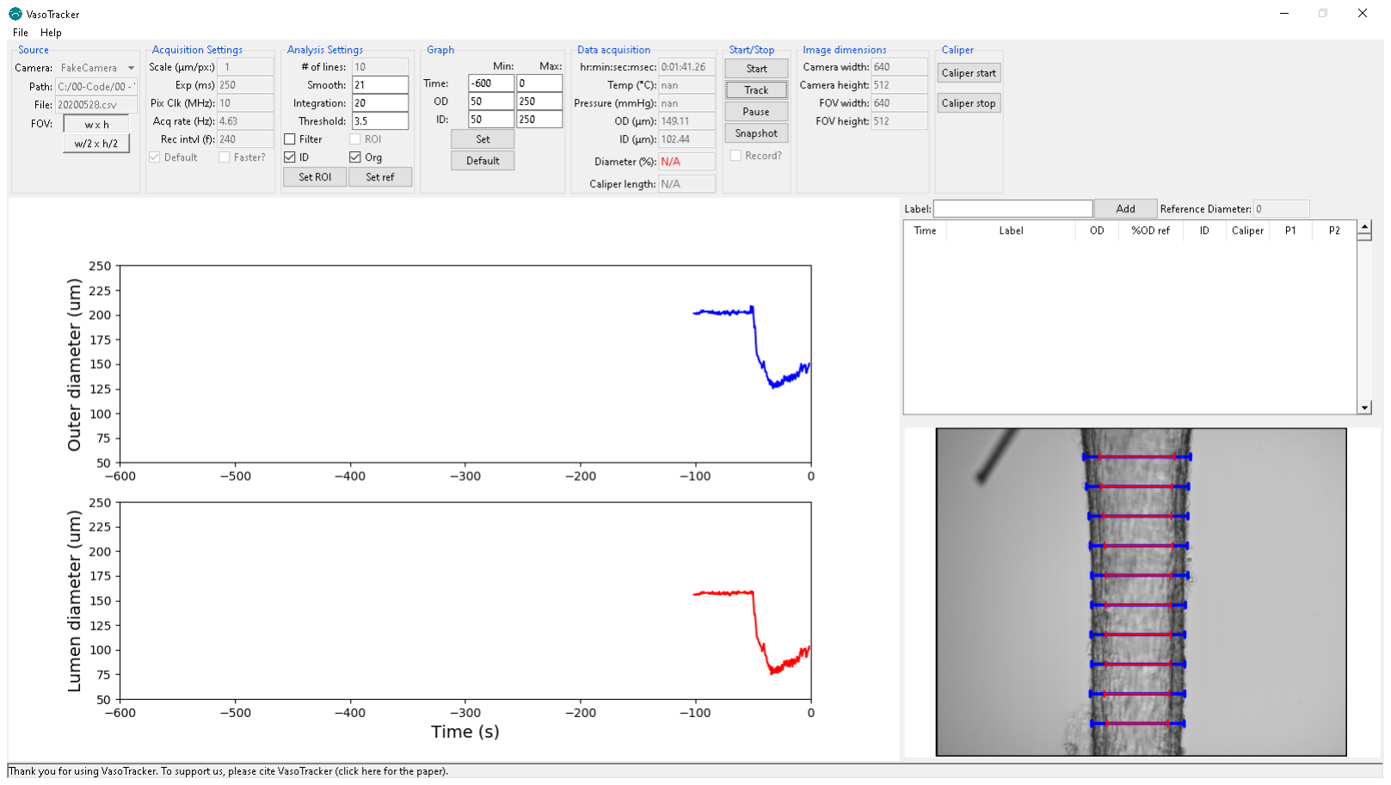
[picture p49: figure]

VASOTRACKER USER MANUAL V1 | 8

Demo Camera Mode

To familiarize users with the VasoTracker Data Acquisition Software, VasoTracker comes bundled with a fake/virtual camera adapter. This virtual camera adapter loads an example video recording of a pressurized artery and displays data as if a real camera is connected.

To run VasoTracker in Demo Mode:

- Enable the Virtual Camera by select “FakeCamera” in the “Source” panel.
- Start the virtual image acquisition by clicking “Start” in the “Start/Stop” panel.
- Begin diameter tracking by clicking “Track” in the “Start/Stop” panel.
- Once diameter tracking has initiated, diameter indicators will be overlaid on the camera feed box (Figure 2) and both inner and outer diameter will be plotted on the live graphs.

Figure 3 – Virtual Camera Mode with diameter tracking

Live Camera Mode

To run VasoTracker in live mode (i.e. acquiring images from a real camera)

- Load your camera by select “Thorlabs” or other camera driver in the “Source” panel.
- Start the image acquisition by clicking “Start” in the “Start/Stop” panel.
- Begin diameter tracking by clicking “Record” in the “Start/Stop” panel.


VASOTRACKER USER MANUAL V1 | 9

## VasoTracker Settings

VasoTracker may have been updated since this section was written. If it has, we should be updating these instructions soon. If you have any queries, send an email to vasotracker@gmail.com.

The settings bar

All of the acquisition and analysis settings can be altered in the settings bar. The settings bar also displays some handy information. Default settings can be changed by editing “default_settings.ini” in the root folder.

Figure 4 – VasoTracker settings bar

Source control panel

Figure 5 – Source settings

Camera: Select your camera here. If you are using a non-standard camera (you must have a working µManager config file), select µManagerCam. To use µManagerCam you mist place your µManager config file in the VasoTracker installation folder.

Path: displays the path to the current working directory.

File: displays the output file name.

FOV: buttons to set the field-of-view. This will only work for some cameras.

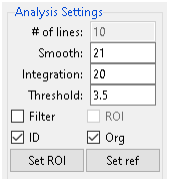
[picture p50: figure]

VASOTRACKER USER MANUAL V1 | 10

Acquisition Settings control panel

Figure 6 – Acquisition settings

Default: Enable/disable the default acquisition settings

Faster?: Enable/disable faster data acquisition here. This is still experimental.

Scale: Set the image calibration here. The default value of one will output diameter value in pixel units.

Exp: Set the camera exposure here.

Pix Clk: set the camera pixel clock here. We have only tested this with the Thorlabs camera. It allows more control over the exposure and frame rate.

Acq rate: displays the current acquisition rate.

Rec intvl: Set the interval (in frames) for exporting images here.

Analysis Settings control panel

Figure 7 – Analysis settings

# of lines: Set the number of scan lines here.

Smooth: Set how much smoothing is applied to intensity profiles (will improve wall detection).

Integration: Set the number of pixel lines over which diameter is integrated.

Threshold: Set threshold value for identifying outliers

Set ROI: Click here to draw an ROI on the display feed, diameter measurement will be limited to this ROI.

Set ref: Click here to set the current diameter as a reference value

Filter: Enable/disable outlier filtering

ROI: Enable/disable the ROI function.

ID: enable/disable inner diameter detection

Org: Slight modification of the tracking algorithm

When editing settings, you must confirm the values entered by hitting the “Enter” button on your keyboard.

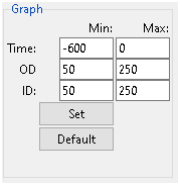
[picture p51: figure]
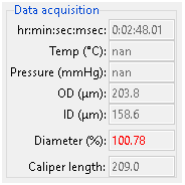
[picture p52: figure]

VASOTRACKER USER MANUAL V1 | 11

Outer and Inner Diameter Graph Settings control panel

Figure 8 – Graph settings

Time: Set the x-axis (time) limits

OD: Set the outer diameter axis limits.

ID: Set the inner diameter axis limits.

Set: Click here to allow an ROI to be drawn on the display feed, diameter measurement will be limited to this ROI.

Default: Click here to set the corresponding graph limits to default values.

All changes to graph settings must be confirmed by hitting the “Enter” button on your keyboard.

Data Acquisition panel

Figure 9 – Data display

Time: Displays the elapsed time (zeroed at beginning of experiment.

Temp: Displays the current temperature (from VasoTracker temperature controller).

Avg Pressure: Displays the vessel pressure (average of readings from VasoTracker pressure sensor).

Outer diameter: Displays the current inner diameter.

Inner diameter: Displays the current inner diameter.

Diameter: Displays the current (outer) diameter as a percentage of the reference diameter.

Caliper length: Displays the length of the manual caliper.


VASOTRACKER USER MANUAL V1 | 12

Start/Stop panel

Figure 10 – Start/stop panel

Start: Starts image acquisition.

Track: Starts the diameter tracking function.

Pause: Pauses diameter tracking (this enables settings to be altered).

Snapshot: Saves a snapshot of the current image display (with and without diameter indicators).

Record?: Enables/disables saving the image feed.

Figure 11 – Example saved images without (middle) and with (right)diameter indicators overlaid.

Image dimension panel

Figure 12 – Image dimensions

Camera width: Displays the width (in pixels) of the camera chip.

Camera height: Displays the height (in pixels) of the camera chip.

FOV width: Displays the width (in pixels) of the current field-of-view.

FOV height: Displays the height (in pixels) of the current field-of-view.

VASOTRACKER USER MANUAL V1 | 13

Image dimension panel

Figure 12 – Image dimensions

Caliper start: pauses image acquisition so that a manual caliper can be drawn on the image

Caliper stop: Does nothing at the moment.

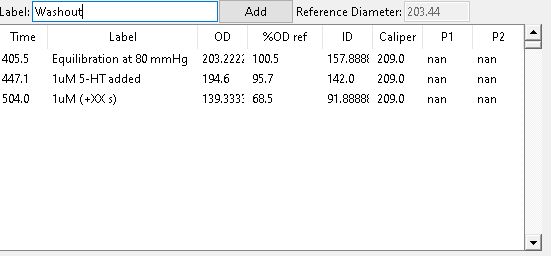
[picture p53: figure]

VASOTRACKER USER MANUAL V1 | 14

## VasoTracker Data Export

Data export

All data is saved automatically. On launching VasoTracker, the user is asked to create a .csv file. At each time point, all experimental parameters (time, average, diameter, pressure, temperature, etc.) are appended to the CSV file.

Individual scanline measurements:

The outer and inner diameter measurements of all scan lines are saved in separate CSV files (“…profiles.csv”).

Spurious measurements:

Whether or not the filtering algorithm is active, all scanline measurement are checked for spurious results. Indicators are saved in the “Flags.csvfiles. ” (1 indicates a good measurement, 0 indicates a spurious measurement). If the filtering algorithm is activated, spurious measurements are not included in the average calculations.

Data entry table

VasoTracker also includes a data entry table (Figure 13). The table allows the user to enter details of any experimental manipulations and provides a convenient measure of arterial tone at the time of each entry. Any data entered into the Data Entry Table (See below) is saved as an additional .csv file, “…tables.csv”.

Figure 13 – Data entry table

VASOTRACKER USER MANUAL V1 | 15

## Editing VasoTracker

VasoTracker is written entirely in the Python programming language. Anybody can edit it in any way they see fit.

Source code installation steps

- Install the prerequisites
- Install Python 2.7 (Anaconda distribution)
- Install Python dependencies

Installing Prerequisites

Before installing VasoTracker, the camera drivers, Arduino IDE, and µManager must be installed. For the Thorlabs DCC1545M camera:

- Download and run the camera driver software from the Thorlabs website: https://www.thorlabs.com/software_pages/ViewSoftwarePage.cfm?Code=ThorCam
- Download and install the latest Nightly Build of µManager from the µManager website: http://valelab4.ucsf.edu/~MM/nightlyBuilds/1.4/Windows/
- Download and install the latest Nightly Build of µManager from the µManager website: http://valelab4.ucsf.edu/~MM/nightlyBuilds/1.4/Windows/

If you edit the VasoTracker source code you will need to run VasoTracker from the python command line or rebuild the application.


VASOTRACKER USER MANUAL V1 | 16

Installing Python 2.7

Should you wish to edit VasoTracker, you need to install Python 2.7. We recommend the Anaconda distribution. Once Python 2.7 has been installed, you also need a number of Python packages.

- Download the 64-bit Windows Anaconda distribution of Python 2.7 from the Anaconda website (we recommend Anaconda 2018.12): https://www.anaconda.com/distribution/
- Launch the installer and click “Next”
- Have a great time reading the License Agreement and click “I Agree”


VASOTRACKER USER MANUAL V1 | 17
- Install for “Just Me”
- Choose the installation directory (and take a note of it)
- Register Anaconda as the default Python 2.7 (but do not add Anaconda to the PATH environment variable!)


VASOTRACKER USER MANUAL V1 | 18
- Have two cups of tea whilst Anaconda installs
- If you want to edit the code, install Microsoft Visual Studio Code
- Click “Finish”


VASOTRACKER USER MANUAL V1 | 19
- Anaconda runs through a special command prompt. It is best to set this to run as administrator. First, locate the folder containing the Anaconda Prompt (search for “Anaconda Prompt” in windows search bar, right click, open file location)
- Right click on the anaconda prompt shortcut (you could also send this shortcut to the desktop, but perform the steps below by right clicking on the desktop shortcut)
- Click properties and open Shortcut tab, then click “Advanced” button
- Check “Run as administrator”


VASOTRACKER USER MANUAL V1 | 20

Installing Python dependencies

The recommended Anaconda distribution comes with most of the Python packages that are required by VasoTracker. Two packages must be installed separately, OpenCV and pyserial.

Installing OpenCV 3.4.1

- Download the OpenCV packaged (.exe file) from the official OpenCV site: https://sourceforge.net/projects/opencvlibrary/files/opencv-win/3.4.1/opencv-3.4.1-vc14_vc15.exe/download (https://sourceforge.net/projects/opencvlibrary/files/opencv-win/3.4.1/opencv-3.4.1-vc14_vc15.exe/download)
- Install OpenCV to C:/OpenCV/
- From the OpenCV directory, copy “cv2.pyd” from:

C:\opencv\build\python\2.7\x64

to the following Anaconda directory:

C:\Users\%Username%\Anaconda2\Lib\site-packages

The Anaconda directory may be in the C:Users\AppData hidden folder. We told you to take a note of it!

Installing pyserial

- Launch Anaconda Prompt


VASOTRACKER USER MANUAL V1 | 21
- Type the following command into the terminal and hit enter:

pip install pyserial

Congratulations if you made it this far, you should now be able to adapt the VasoTracker source code using Visual Studio Code, or any other editor.

Launching VasoTracker from the source code

VasoTracker should be launched from the Anaconda Prompt.

- Launch Anaconda Prompt

VASOTRACKER USER MANUAL V1 | 22
- Navigate to the VasoTracker source code folder using the “cd” command, by typing the following into the prompt and hitting enter:

cd c:\VasoTracker-master\VasoTracker_Software\Source

- Launch VasoTracker by typing the following into the prompt and hitting enter:

python vasotracker.py


www.vasotracker.com

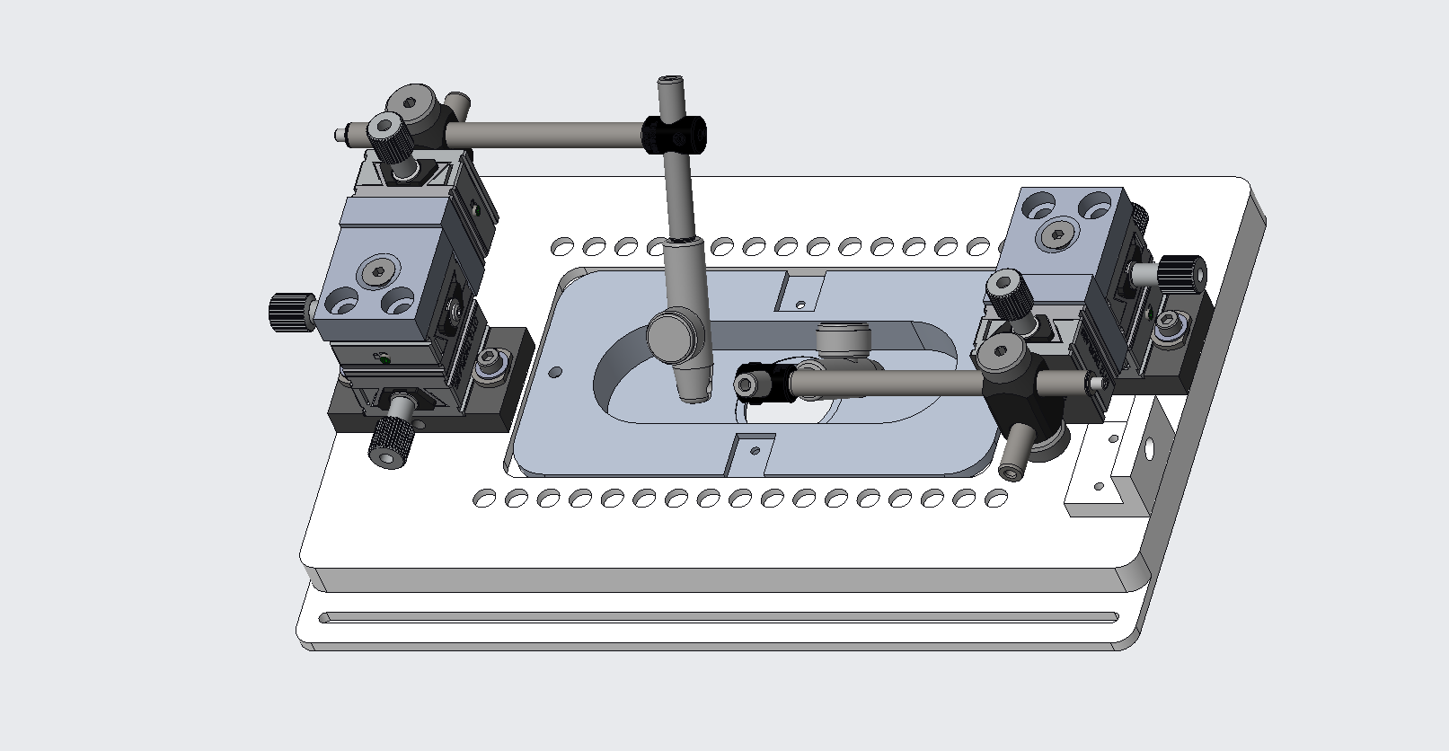
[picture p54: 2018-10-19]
VasoTracker_Vessel_Chamber/Images/vasotracker_assembly.tif

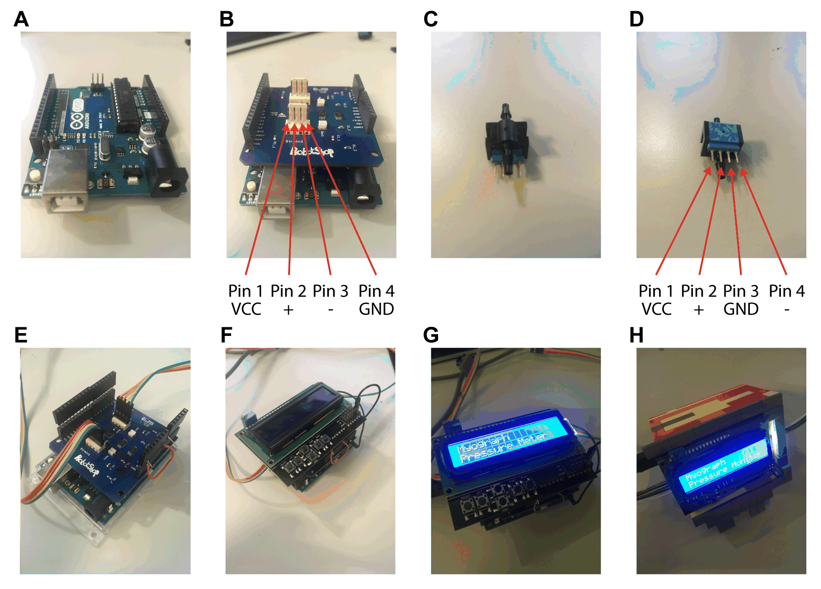
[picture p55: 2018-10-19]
VasoTracker_Pressure_Monitor/Images/Pressure Monitor Construction.gif

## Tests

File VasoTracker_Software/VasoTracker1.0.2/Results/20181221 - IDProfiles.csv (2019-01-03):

Time (s) | Profile 1 | Profile 2 | Profile 3 | ...

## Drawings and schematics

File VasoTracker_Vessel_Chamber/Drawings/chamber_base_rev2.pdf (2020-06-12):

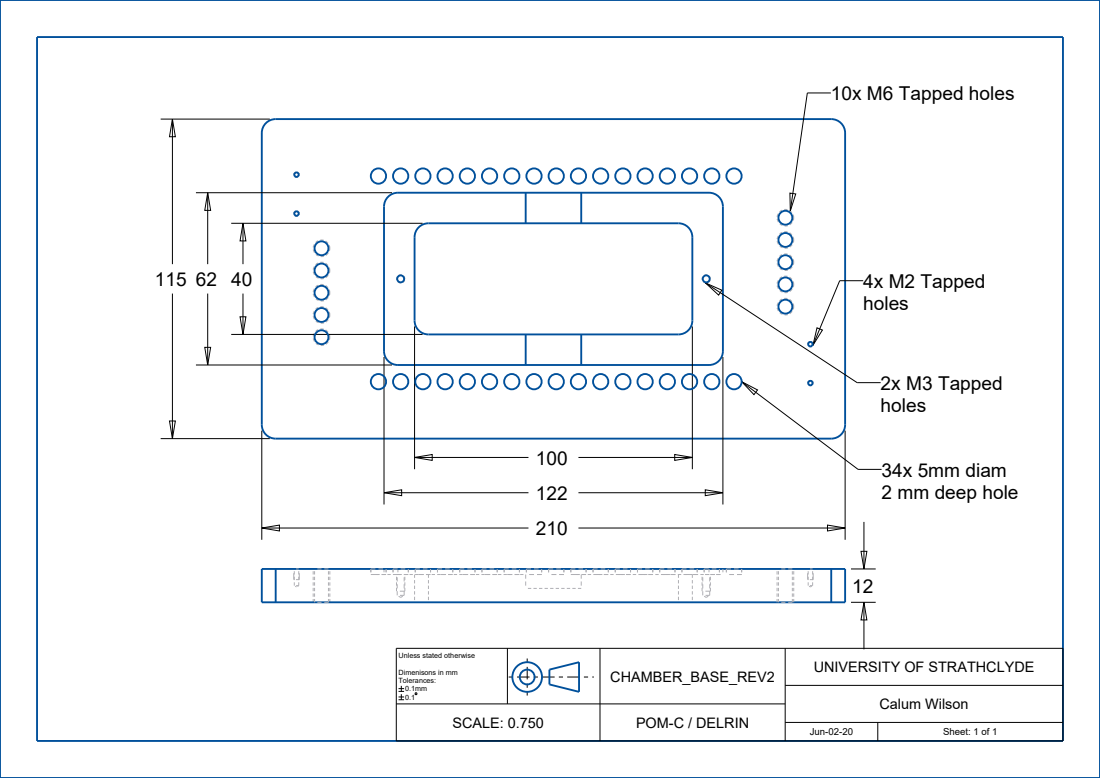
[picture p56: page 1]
Calum Wilson; CHAMBER_BASE_REV2; Unless stated otherwise; Dimenisons in mm Tolerances: 0.1mm 0.1; 10x M6 Tapped holes; 4x M2 Tapped holes; 2x M3 Tapped holes

34x 5mm diam
2 mm deep hole

UNIVERSITY OF STRATHCLYDE

SCALE: 0.750 | POM-C / DELRIN

Jun-02-20 | Sheet: 1 of 1

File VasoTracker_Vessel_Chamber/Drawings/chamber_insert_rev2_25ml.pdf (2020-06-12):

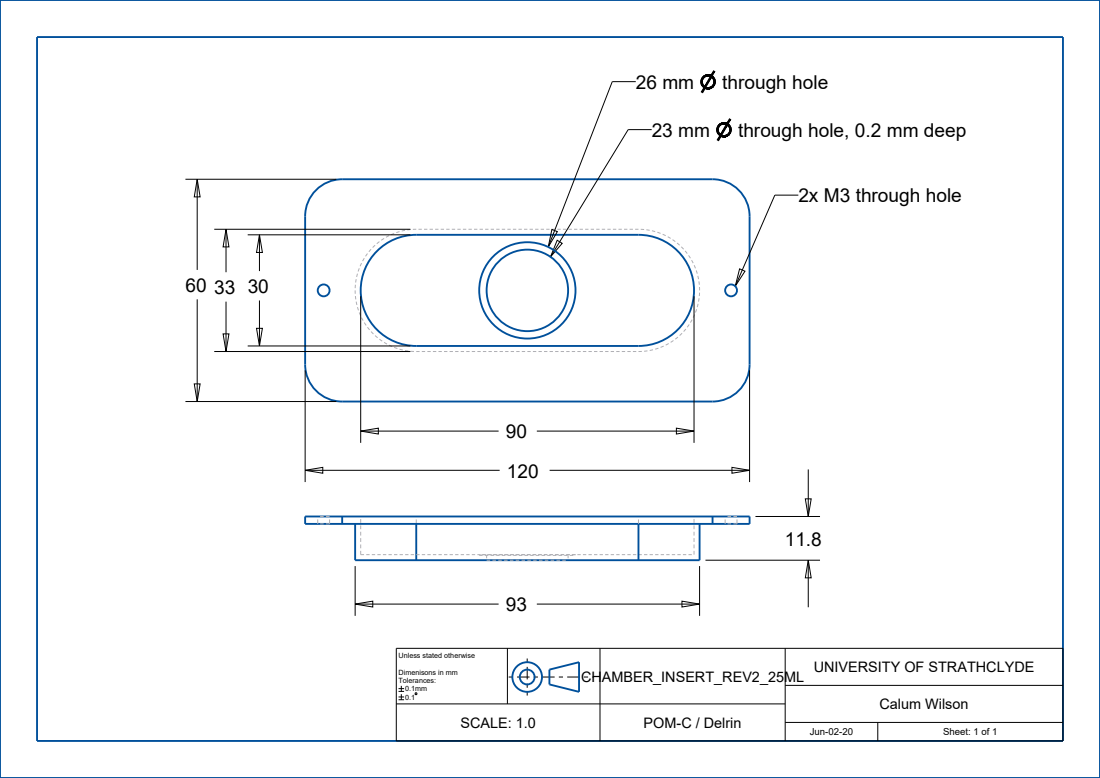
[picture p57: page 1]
Calum Wilson; CHAMBER_INSERT_REV2_25ML; Unless stated otherwise; Dimenisons in mm Tolerances: 0.1mm 0.1; 2x M3 through hole

26 mm through hole
23 mm through hole, 0.2 mm deep

UNIVERSITY OF STRATHCLYDE

SCALE: 1.0 | POM-C / Delrin

Jun-02-20 | Sheet: 1 of 1

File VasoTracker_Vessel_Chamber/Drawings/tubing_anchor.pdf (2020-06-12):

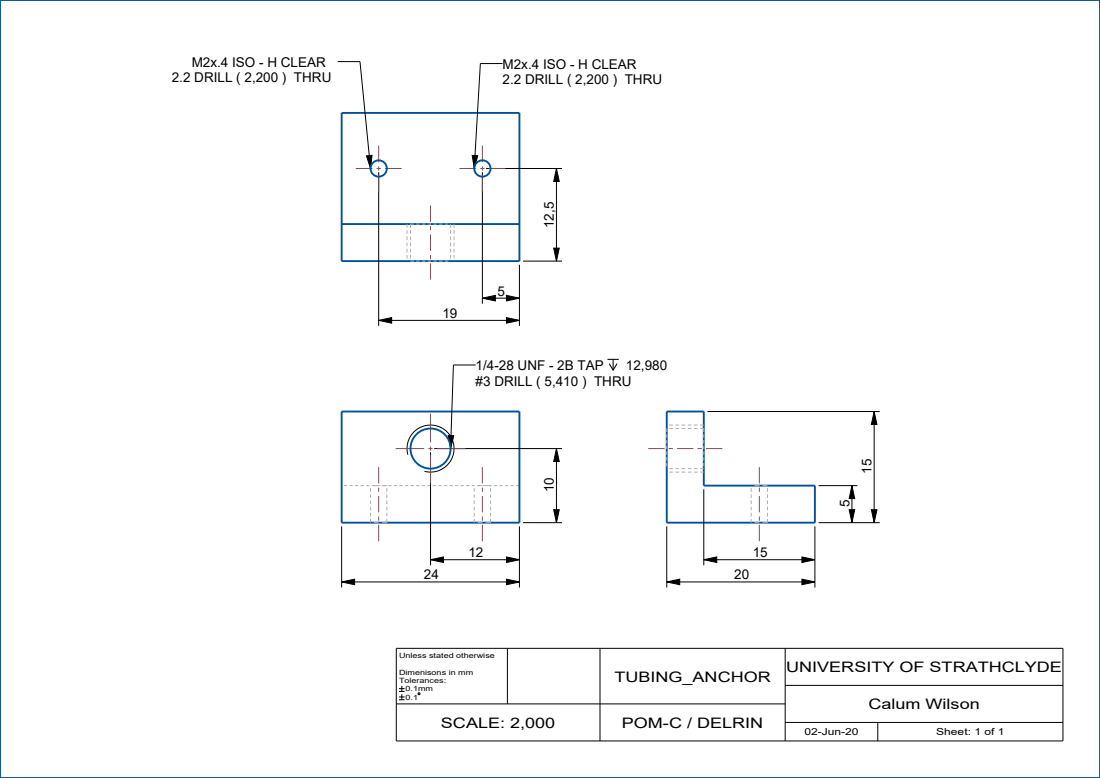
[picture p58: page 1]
02-Jun-20; Sheet: 1 of 1 SCALE: 2,000; POM-C / DELRIN; Calum Wilson; TUBING_ANCHOR; Unless stated otherwise; Dimenisons in mm Tolerances: 0.1mm 0.1; 1/4-28 UNF - 2B TAP; #3 DRILL ( 5,410 ) THRU; M2x.4 ISO - H CLEAR 2.2 DRILL ( 2,200 ) THRU

UNIVERSITY OF STRATHCLYDE

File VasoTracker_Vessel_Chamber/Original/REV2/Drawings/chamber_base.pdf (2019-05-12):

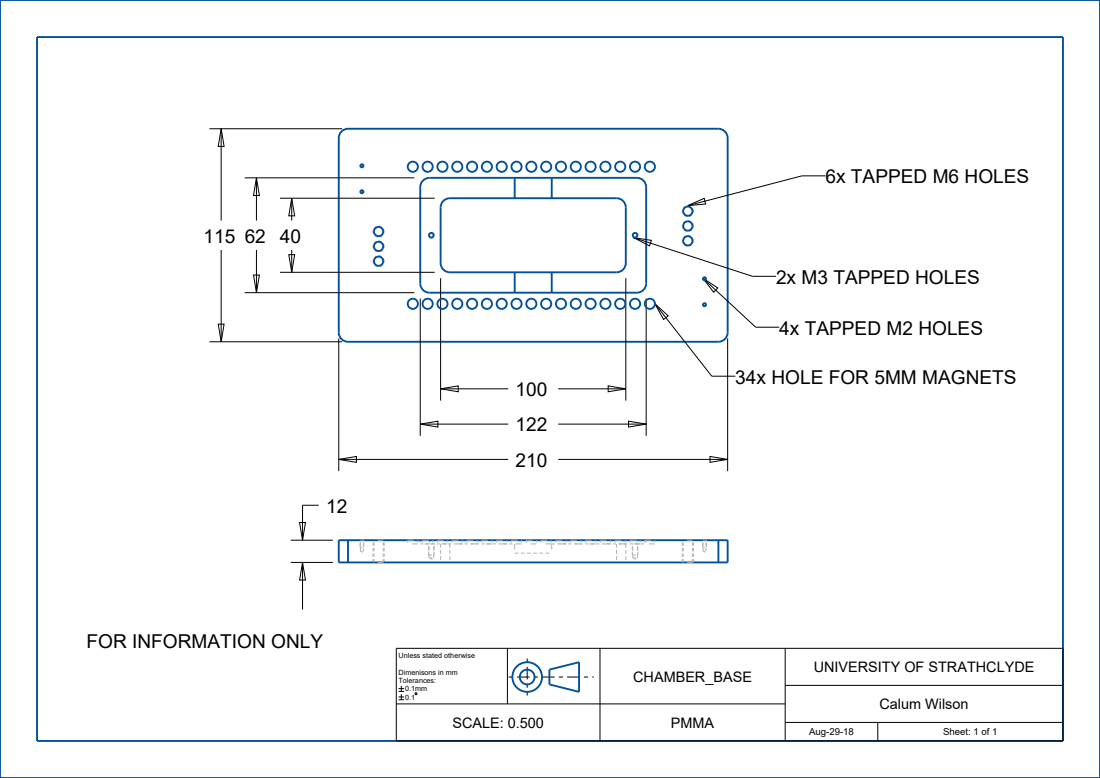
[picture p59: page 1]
Calum Wilson; CHAMBER_BASE; Unless stated otherwise; Dimenisons in mm Tolerances: 0.1mm 0.1; 6x TAPPED M6 HOLES; 2x M3 TAPPED HOLES

4x TAPPED M2 HOLES
34x HOLE FOR 5MM MAGNETS

FOR INFORMATION ONLY

UNIVERSITY OF STRATHCLYDE

SCALE: 0.500 | PMMA

Aug-29-18 | Sheet: 1 of 1

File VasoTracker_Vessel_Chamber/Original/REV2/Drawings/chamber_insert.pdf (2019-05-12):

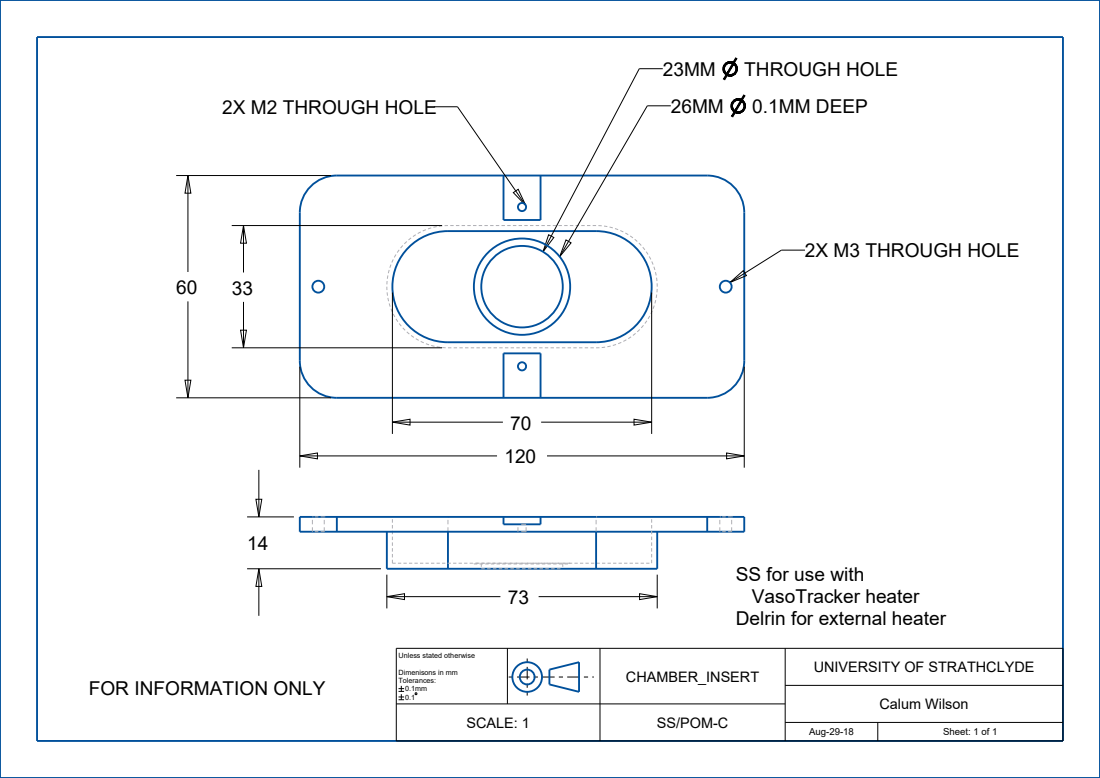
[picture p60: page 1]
Calum Wilson; CHAMBER_INSERT; Unless stated otherwise; Dimenisons in mm Tolerances: 0.1mm 0.1; 26MM 0.1MM DEEP; 23MM THROUGH HOLE; 2X M3 THROUGH HOLE; 2X M2 THROUGH HOLE

SS for use with
VasoTracker heater
Delrin for external heater

UNIVERSITY OF STRATHCLYDE

FOR INFORMATION ONLY

SCALE: 1 | SS/POM-C

Aug-29-18 | Sheet: 1 of 1

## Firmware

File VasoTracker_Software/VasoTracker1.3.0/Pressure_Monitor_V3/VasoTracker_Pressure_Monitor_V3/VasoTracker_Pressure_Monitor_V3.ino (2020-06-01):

/* VasoTracker Pressure Monitor Code: Dr. N8-Style*/
/* This code was written by Calum Wilson with help from Penny Lawton.*/
/* It was made significantly better by Nathan Tykocki.*/

//  Include the LCD, wheatstone bridge, and stepper motor support libraries and headers
#include <LiquidCrystal.h>
#include "pressure.h" //This file should be in the working folder. It now contains all the wheatstone bride headers and associated info (from here: https://github.com/RobotShop/Wheatstone-Bridge-Amplifier-Shield/archive/master.zip).

//  Initialize the library with the numbers of the interface pins
LiquidCrystal lcd(8, 9, 4, 5, 6, 7);

//  Initial calibration values for force transducer
const int CST_PRESSURE_IN_MIN = 350;     // Raw value calibration lower point
const int CST_PRESSURE_IN_MAX = 650;     // Raw value calibration upper point
const int CST_PRESSURE_OUT_MIN = 0;      // Pressure calibration lower point
const int CST_PRESSURE_OUT_MAX = 200;    // Pressure calibration upper point. This is in mmHg. This is about the max it can do.
const int CST_CAL_PRESSURE_MIN = 0;      // As with before, in mmHg.
const int CST_CAL_PRESSURE_MAX = 200;    // As with before, in mmHg.
const int CST_CAL_STEP_SM = 1;           // Change this to change what the L/R buttons do during calibration.
const int CST_CAL_STEP_LG = 10;          // Change this to change what the U/D buttons do during calibration.

//  Setup the data recording (data to be sent out, sampling rate)
//******************************************************************************************************************
  #define       NUMSAMPLES 5               //  Change this to alter the number of samples averaged.                *
  unsigned long TIME_DELAY = 5;           //  Change this to alter the time delay for wheatstone bridge output.   *
  unsigned long LCD_TIME_DELAY = 500;           // Setting a delay to update the LCD screen
//******************************************************************************************************************

uint16_t      samples1[NUMSAMPLES];      // Needed to determine how the samples will be summed and averaged.
uint16_t      samples2[NUMSAMPLES];      // Needed to determine how the samples will be summed and averaged.
unsigned long previousMillis = 0;        // Resetting the clock to determine how much time has elapsed.
unsigned long initMillis = 0;            // Resetting the clock to determine how much time has elapsed.
unsigned long elapsedMillis = 0;
bool update_flag = 0;                    // Flag to update the LCD display

//  Initialize the Wheatstone bridge object, plugged into Strain2 on the shield
WheatstoneBridge wsb1(A1, CST_PRESSURE_IN_MIN, CST_PRESSURE_IN_MAX, CST_PRESSURE_OUT_MIN, CST_PRESSURE_OUT_MAX);

//  Initialize the Wheatstone bridge object, plugged into Strain2 on the shield
WheatstoneBridge wsb2(A0, CST_PRESSURE_IN_MIN, CST_PRESSURE_IN_MAX, CST_PRESSURE_OUT_MIN, CST_PRESSURE_OUT_MAX);

//  All Setup functions go in here: calibrate transducer, regulate everything, etc.
void setup()
{
  //  Transducer 1: Calibration and variables needed for linear interpolation
  int cal_adc_low = CST_PRESSURE_IN_MIN;
  int cal_adc_high = CST_PRESSURE_IN_MAX;
  int cal_pressure_low = CST_PRESSURE_OUT_MIN;
  int cal_pressure_high = CST_PRESSURE_OUT_MAX;
  
  //  Initialize LCD screen and intro
  lcd.begin(16, 2); displayScreen("VasoTracker", "Pressure Monitor"); delay(1000);

  //Calibrate the first pressure transducer!
  displayScreen("* Calibration *", "Transducer 1"); delay(1000);
  
  // Calibration 1: low value. Get low pressure value and associated ADC value.
  displayScreen("* Calibration *", "Low value"); delay(1000);
  cal_pressure_low   = getValueInRange("Set low pressure", "Pres (mmHg):", 13, cal_pressure_low, CST_CAL_PRESSURE_MIN, CST_CAL_PRESSURE_MAX, CST_CAL_STEP_SM, CST_CAL_STEP_LG);
  cal_adc_low     = getValueADC("Set low raw ADC", "Raw ADC:", 13, A1, btnSELECT);

  // Calibration 1: high value. Get high pressure value and associated ADC value.
  displayScreen("* Calibration *", "High value"); delay(1000);
  cal_pressure_high  = getValueInRange("Set high pressure", "Pres (mmHg):", 13, cal_pressure_high, CST_CAL_PRESSURE_MIN, CST_CAL_PRESSURE_MAX, CST_CAL_STEP_SM, CST_CAL_STEP_LG);
  cal_adc_high    = getValueADC("Set high raw ADC", "Raw ADC:", 13, A1, btnSELECT);

  //  Peform linear calibration based on values chosen and selected above for transducer 1.
  wsb1.linearCalibration(cal_adc_low, cal_adc_high, cal_pressure_low, cal_pressure_high);
  
  //  Transducer 2: Calibration and variables needed for linear interpolation
  int cal_adc_low2 = CST_PRESSURE_IN_MIN;
  int cal_adc_high2 = CST_PRESSURE_IN_MAX;
  int cal_pressure_low2 = CST_PRESSURE_OUT_MIN;
  int cal_pressure_high2 = CST_PRESSURE_OUT_MAX;
  
  //Calibrate the secondpressure transducer!  
  displayScreen("* Calibration *", "Transducer 2"); delay(1000);
  
  // Calibration 2: Low value. Get low pressure value and associated ADC value.
  displayScreen("* Calibration *", "Low value"); delay(1000);
  cal_pressure_low2   = getValueInRange("Set low pressure", "Pres (mmHg):", 13, cal_pressure_low2, CST_CAL_PRESSURE_MIN, CST_CAL_PRESSURE_MAX, CST_CAL_STEP_SM, CST_CAL_STEP_LG);
  cal_adc_low2     = getValueADC("Set low raw ADC", "Raw ADC:", 13, A0, btnSELECT);

  // Calibration 2: high value. Get high pressure value and associated ADC value.
  displayScreen("* Calibration *", "High value"); delay(1000);
  cal_pressure_high2 = getValueInRange("Set high pressure", "Pres (mmHg):", 13, cal_pressure_high2, CST_CAL_PRESSURE_MIN, CST_CAL_PRESSURE_MAX, CST_CAL_STEP_SM, CST_CAL_STEP_LG);
  cal_adc_high2 = getValueADC("Set high raw ADC", "Raw ADC:", 13, A0, btnSELECT);

  //  Peform linear calibration based on values chosen and selected above for transducer 2.
  wsb2.linearCalibration(cal_adc_low2, cal_adc_high2, cal_pressure_low2, cal_pressure_high2);
  
  //  Initialize serial communication and set display labels.
  // Setup display labels
  Serial.begin(9600);
  lcd.begin(16,2);
  displayScreen("P1 (mmHg):", "P2 (mmHg):");
}

//  Defining void loops to do the dirty work. The first one pulls the number of samples needed from both transducers and averages them separately. Time is set above.
void pressure(bool update_flag){
  uint8_t i;
  float avg1;
  float avg2;
  unsigned long currentMillis = millis();
  
  if ((currentMillis - previousMillis) >= TIME_DELAY){
    
    for (i = 0; i < NUMSAMPLES; i++){
      samples1[i] = wsb1.measureForce();
      samples2[i] = wsb2.measureForce();
    }
    
    avg1 = 0;
    avg2 = 0;
    
    for (i = 0; i < NUMSAMPLES; i++){
      avg1 += samples1[i];
      avg2 += samples2[i];
    }
    
    avg1 /= NUMSAMPLES;
    avg2 /= NUMSAMPLES;    

    if (update_flag == 1){
      lcd.setCursor(11, 0); lcd.print(avg1);
      lcd.setCursor(11, 1); lcd.print(avg2);
    }
    previousMillis = currentMillis;
  }

  Serial.print("<P1"); Serial.print(":"); Serial.print(avg1);  Serial.print(";");
  Serial.print("P2");  Serial.print(":"); Serial.print(avg2); Serial.print(";"); Serial.println(">");
  
}

//If you want to do more things it's easy to add the loops here. Like if you wanted to do only 1 transducer and add temperature controls to a single unit...
unsigned long currentMillis_LCD = millis();
void loop(){
  currentMillis_LCD = millis(); //Get the current time
  elapsedMillis = currentMillis_LCD - initMillis;
  
  if (elapsedMillis > LCD_TIME_DELAY){
    initMillis = currentMillis_LCD;
    update_flag = 1;
  }
  
  pressure(update_flag);  // Get the current pressure values
  update_flag = 0;
}

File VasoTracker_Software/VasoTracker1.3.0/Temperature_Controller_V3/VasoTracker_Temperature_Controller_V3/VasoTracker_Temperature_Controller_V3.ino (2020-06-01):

/* VasoTracker Temperature Controller Code: Dr. N8-Style*/
/* This code was written by Calum Wilson.*/
/* It was made significantly better with input from Nathan Tykocki.*/

//  Include the LCD, wheatstone bridge, and stepper motor support libraries and headers
#include <LiquidCrystal.h> // Include the LCD library

// Initialize the library with the numbers of the interface pins
LiquidCrystal lcd(8, 9, 4, 5, 6, 7); 
#define btnRIGHT 0
#define btnUP 1
#define btnDOWN 2
#define btnLEFT 3
#define btnSELECT 4
#define btnNONE 5
#define btnUNKNOWN 6

// Initialize the thermistor values
#define thermistor_pin A0 // which analog thermistor input pin // Normally A0 or A2
#define nominal_temp 25 // nominal resistance temperature (almost always 25 C)   
#define nominal_resistance 10000 // nominal  resistance at nominal resistance temperature   
#define beta_coeff 3950 // beta coefficient of the thermistor
#define series_resistor 10000 // the value of the 'other' resistor    
#define output_pin  3

//  Setup the data recording (data to be sent out, sampling rate)
//******************************************************************************************************************
  #define       NUMSAMPLES 5               //  Change this to alter the number of samples averaged.                *
  unsigned long TIME_DELAY = 5;            //  Change this to alter the time delay for wheatstone bridge output.   *
  unsigned long LCD_TIME_DELAY = 500;      // Setting a delay to update the LCD screen

  #define initial_set_point 25.0 // initial set point
  int min_temp = 20;
  int max_temp = 40;
//******************************************************************************************************************


uint16_t      samples[NUMSAMPLES];      // Needed to determine how the samples will be summed and averaged.
unsigned long previousMillis = 0;        // Resetting the clock to determine how much time has elapsed.
unsigned long initMillis = 0;            // Resetting the clock to determine how much time has elapsed.
unsigned long elapsedMillis = 0;
bool update_flag = 0;                    // Flag to update the LCD display
double setpoint, test, cal_temp_low;


// Function for reading the keypad
int readkeypad(){
  int adc_key_in = analogRead(A0); //Normally 5 or 0
  int ret = btnUNKNOWN;
  
  if (adc_key_in < 50) ret = btnRIGHT;
  if ( (adc_key_in > 50) && (adc_key_in < 250) ) ret = btnUP;
  if ( (adc_key_in > 250) && (adc_key_in < 450) ) ret = btnDOWN;
  if ( (adc_key_in > 450) && (adc_key_in < 650) ) ret = btnLEFT;
  if ( (adc_key_in > 650) && (adc_key_in < 850) ) ret = btnSELECT;
  if (adc_key_in > 850) ret = btnNONE; 
  return ret;
 }

void displayScreen(char row1[], char row2[])
{
  lcd.clear();
  lcd.setCursor(0, 0); lcd.print(row1);
  lcd.setCursor(0, 1); lcd.print(row2);
}

// Setup function
void setup()
{
  // Initialize LCD screen and intro
  lcd.begin(16, 2); displayScreen("VasoTracker", "Temp Controller"); delay(1000);
  
  // Main screen
  displayScreen("Set (*C):  ", "Act (*C):  ");
  
  Serial.begin(9600);

  // Setpoint
  setpoint = initial_set_point;

  //Set the output pin
  pinMode(output_pin, OUTPUT);
}

// < Main program loop >
void temperature(bool update_flag, double setpoint) {
  uint8_t i;
  float ADC_average;
  float resistance;
  float temperature;
  unsigned long currentMillis = millis();
  
  if ((currentMillis - previousMillis) >= TIME_DELAY){
  
  // Take readings
  for (i = 0; i < NUMSAMPLES; i++){
    samples[i] = analogRead(thermistor_pin);
  }
  
  // Sum readings
  ADC_average = 0;
  for (i = 0; i < NUMSAMPLES; i++){
    ADC_average += samples[i];
  }

  // Average the readings
  ADC_average /= NUMSAMPLES;
  
  // Convert the voltage drop over the thermistor to resistance using the Steinhart equation
  // However, remember that the analogPorts don't give a voltage, but an ADC value...
  resistance = series_resistor / ((1023 / ADC_average) - 1);
  temperature = 1/( log(resistance / nominal_resistance)/beta_coeff + (1.0 / (nominal_temp + 273.15)) ) - 273.15 ;            
 
  // Display temperature values
  if (update_flag == 1){
    lcd.setCursor(11, 0); lcd.print(setpoint);
    lcd.setCursor(11, 1); lcd.print(temperature);
  }

  // Turn on/off the output pin(s)
  if (setpoint > temperature){
    digitalWrite(output_pin, HIGH);
  } 
  else {
    digitalWrite(output_pin, LOW);
  }

  }


  // Print to the serial Port
  // Do not change this, as it needs to be this format for VasoTracker
  Serial.print("<T1"); Serial.print(":"); Serial.print(temperature); Serial.print(";");
  Serial.print("T2"); Serial.print(":"); Serial.print(setpoint); Serial.print(";"); Serial.println(">");
  //Serial.flush(); // Can't remember if this is required or not
}







//If you want to do more things it's easy to add the loops here. Like if you wanted to do only 1 transducer and add temperature controls to a single unit...
unsigned long currentMillis_LCD = millis();
void loop(){
  
  //Get the current time
  currentMillis_LCD = millis();
  elapsedMillis = currentMillis_LCD - initMillis;

  // Check if we should update display
  if (elapsedMillis > LCD_TIME_DELAY){
    initMillis = currentMillis_LCD;
    update_flag = 1;
  


    // Check if any of the LCD shield buttons have been pressed
    int lcd_button_adc = analogRead(A0);
    int buttons2 = readkeypad();
    switch(buttons2){
      
      case btnUP:
        setpoint += 1;
        if(setpoint > max_temp)
          setpoint = max_temp;
        break;
        
      case btnRIGHT:
        setpoint += 0.5;
        if(setpoint > max_temp)
          setpoint = max_temp;
        break;
  
      case btnDOWN:
        setpoint -= 1;
        if(setpoint < min_temp)
          setpoint = min_temp;
        break;
  
      case btnLEFT:
        setpoint -= 0.5;
        if(setpoint < min_temp)
          setpoint = min_temp;
        break;
    }
   }

  // Get the current temperature
  temperature(update_flag, setpoint);
  update_flag = 0;
}

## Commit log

2018-10-19 Pressure monitor
2018-10-19 Vessel chamber
    [VasoTracker_ChamberBase.stp, VasoTracker_ChamberInsert.stp, VasoTracker_TubingAnchor.stp, chamber_base.prt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]
2019-01-03 V1.0.2 release
    [20181221 - IDProfiles.csv, 20181221 - ODProfiles.csv, 20181221 - Table.csv, 20181221.csv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]
2019-04-16 Temperature sensor code fixed
    Enable buttons on LCD panel
2019-04-16 Temp controller instruction update
    [Arduino Temp Controller - Updated 20190416.fzz]
2019-05-12 updating bath files
    [VasoTracker_ChamberBase.stp, VasoTracker_ChamberInsert.stp, VasoTracker_TubingAnchor.stp, chamber_base.prt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]
2019-05-12 Updated VasoTracker chamber
    [chamber_base.igs, chamber_base.prt, chamber_base.stp, chamber_insert.igs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]
2020-06-01 Update to v1.2.0
    [20200528 - IDFlags.csv, 20200528 - IDProfiles.csv, 20200528 - ODFlags.csv, 20200528 - ODProfiles.csv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]
2020-06-12 Vessel chamber 2
    [VasoTracker_ChamberBase.stp, VasoTracker_ChamberInsert.stp, VasoTracker_TubingAnchor.stp, chamber_base.igs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]
2020-06-12 update read me
    [CANNULA_ARM_A v1.f3d, CANNULA_ARM_A v1.step, CANNULA_ARM_A v1.stl, CANNULA_ARM_B v1.f3d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]
2020-08-17 NI control
    [20200610 - IDFlags.csv, 20200610 - IDProfiles.csv, 20200610 - ODFlags.csv, 20200610 - ODProfiles.csv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]
